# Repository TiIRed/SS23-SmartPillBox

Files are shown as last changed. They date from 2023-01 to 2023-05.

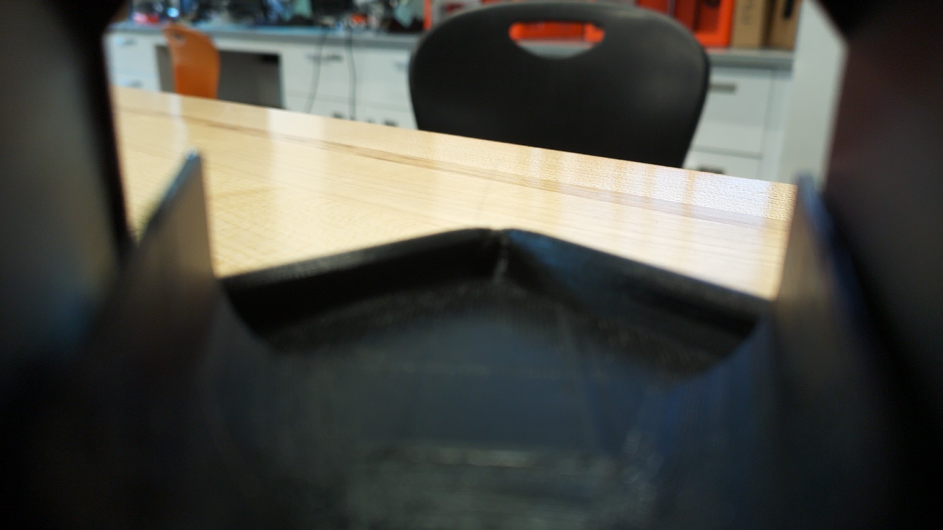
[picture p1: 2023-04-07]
Pi_Controls/test.jpg

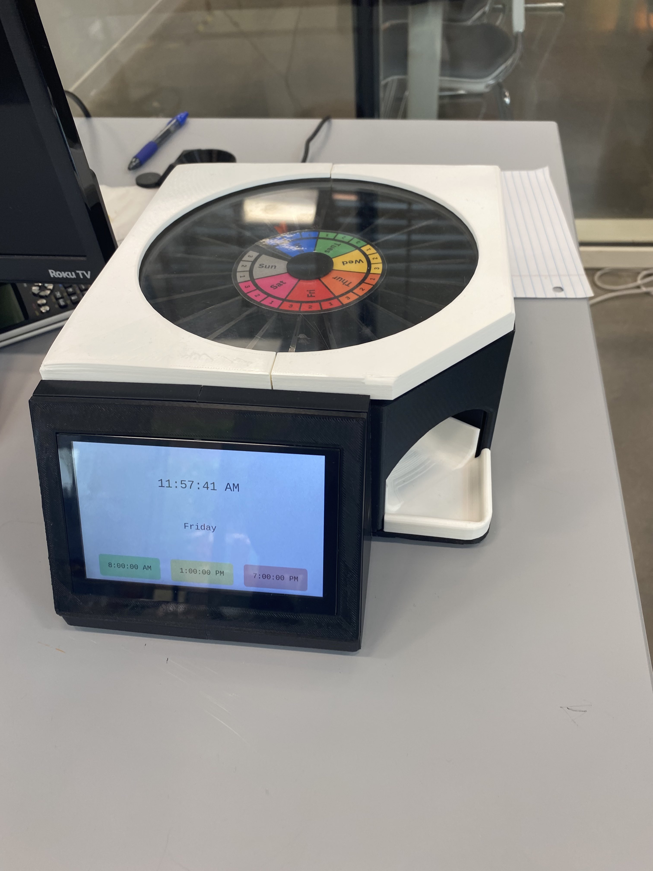
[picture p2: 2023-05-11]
Photos_Videos/IMG_7056.jpg

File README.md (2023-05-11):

# SS23-SmartPillBox

Pillbox
Download NodeJS at https://nodejs.org/en/download.
Navigate to the HTML folder and delete the node_modules folder and run "npm install" to install the modules again.
We found that when changing environments it was easier to install all of the modules again.

To start the program, run "npm run start".

The program can also be made into an executable by using electron forge (https://www.electronforge.io/) and can be compiled for a number of systems.

Server
First navigate to the ServerFile and run .venv\Scripts\activate to enter the virtual environment
For demonstration purposes and because we were unable to configure our server in the way that we like. The web app was deployed using waitress and can be called with the function "waitress-serve --call 'app:create_app'"

the storage variables are in appdata/roaming/html/config or home/.config/HTML
and when running npm on the pi you just have to do: rm node_modules && npm install

Database
Download PSQL from https://www.postgresql.org/download/ and make sure to Download PGAgent and PGBouncer from the stack builder
Next download pgAdmin at https://www.pgadmin.org/download/ this will let us manage the database.

Here you can create a new databse on the postgresql server that was just created. First I suggest creating a new user role that can access and edit the database.

For the included code I used the following SQL script
```
CREATE ROLE sfransen WITH
    LOGIN
    SUPERUSER
    INHERIT
    CREATEDB
    CREATEROLE
    NOREPLICATION
    PASSWORD Ladybug
```
Then I created the Database with:
```
CREATE DATABASE pillbox
    WITH
    OWNER = sfransen
    ENCODING = 'UTF8'
    LC_COLLATE = 'English_United States.1252'
    LC_CTYPE = 'English_United States.1252'
    TABLESPACE = pg_default
    CONNECTION LIMIT = -1
    IS_TEMPLATE = False;
GRANT TEMPORARY, CONNECT ON DATABASE pillbox TO PUBLIC;
GRANT ALL ON DATABASE pillbox TO sfransen;
```
Finally I created the tables with:
```
CREATE TABLE IF NOT EXISTS public.logins
(
    id bigint NOT NULL DEFAULT 'nextval('logins_id_seq'::regclass)',
    fname character varying(200) COLLATE pg_catalog."default" NOT NULL,
    lname character varying(200) COLLATE pg_catalog."default" NOT NULL,
    email character varying(200) COLLATE pg_catalog."default" NOT NULL,
    password character varying(200) COLLATE pg_catalog."default" NOT NULL,
    mtime time without time zone NOT NULL,
    mdtime time without time zone NOT NULL,
    etime time without time zone NOT NULL,
    CONSTRAINT logins_pkey PRIMARY KEY (id),
    CONSTRAINT logins_email_key UNIQUE (email)
)

TABLESPACE pg_default;
ALTER TABLE IF EXISTS public.logins
    OWNER to sfransen;
```
```
CREATE TABLE IF NOT EXISTS public.medications
(
    id bigint NOT NULL DEFAULT 'nextval('medications_id_seq'::regclass)',
    name character varying(200) COLLATE pg_catalog."default" NOT NULL,
    quantity bigint NOT NULL DEFAULT 'nextval('medications_quantity_seq'::regclass)',
    time_name character varying(200) COLLATE pg_catalog."default" NOT NULL,
    days text[] COLLATE pg_catalog."default" NOT NULL,
    username character varying(200) COLLATE pg_catalog."default",
    CONSTRAINT medications_pkey PRIMARY KEY (id)
)

TABLESPACE pg_default;
ALTER TABLE IF EXISTS public.medications
    OWNER to sfransen;
```
```
CREATE TABLE IF NOT EXISTS public.photos
(
    id bigint NOT NULL DEFAULT 'nextval('photos_id_seq'::regclass)',
    data bytea NOT NULL,
    "time" character varying(200) COLLATE pg_catalog."default" NOT NULL,
    username character varying(200) COLLATE pg_catalog."default" NOT NULL,
    dayofweek character varying(200) COLLATE pg_catalog."default" NOT NULL,
    CONSTRAINT photos_pkey PRIMARY KEY (id)
)

TABLESPACE pg_default;

ALTER TABLE IF EXISTS public.photos
    OWNER to sfransen;
```

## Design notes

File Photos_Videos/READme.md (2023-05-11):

Photos and Videos from the demonstration and assembly.

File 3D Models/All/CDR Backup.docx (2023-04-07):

Critical Design Review

ECEN 4024: Smart Pill Box Team

Spring 2023

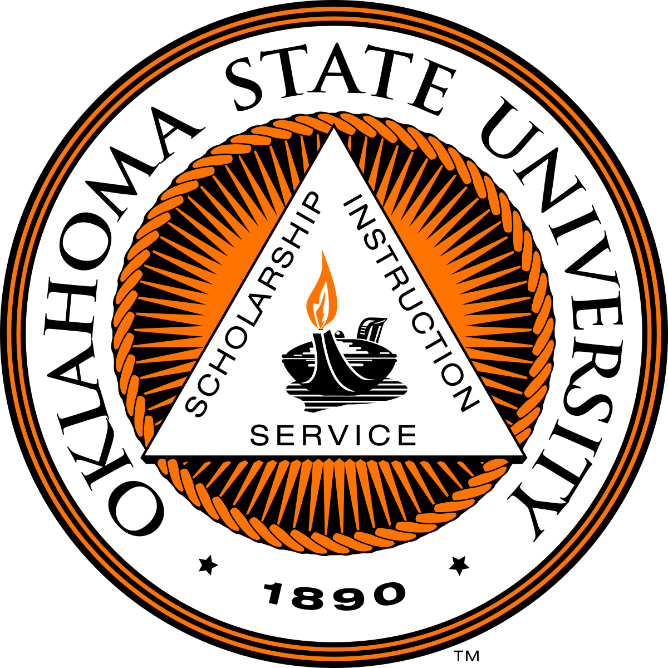
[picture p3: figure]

Report Presented by:

Zarek Rooker

Daniel Jacobs

Zahra Alnahwi

Stephen Fransen

Advisors:

Dr. Weihua Sheng, Joel Quarnstrom (GA), Su Zhidong (GA)

Electrical and Computer Engineering

Oklahoma State University

# 1. Team

## 1.1 Team Structure

- Zarek Rooker
  - Role: Hardware Manager & POC
  - Assignment: Hardware Design, Electronic Testing
- Zahra Alnahwi
  - Role: Circuit Designer:
  - Assignment: Electronic Design & Testing
- Stephen Fransen
  - Role: Backend Dev
  - Assignment: Software, Server Building
- Daniel Jacobs
  - Role: UI Designer:
  - Assignment: Software, User Interface

## 1.2 Advisors

The project is advised by Dr. Weihua Sheng and Graduate Assistants Joel Quarnstrom and Su Zhidong. Both graduate assistants offer advice and explanation. Joel offers advice in hardware design and testing while Su assists in electronic and software advice.

# 2. Problem Objective

The main vision of this project is to provide an efficient and safe way to manage medication for elderly patients, especially those with cognitive decline, memory loss, and visual impairments. The Smart Pill Box (SPB) can help them to take medication correctly and on time, reduce medication errors, and provide a better way for caregivers to monitor the medication adherence. The SPB can also provide a more convenient, user-friendly, and cost-effective solution compared to other existing solutions.

# 3. Design Constraints

## 3.1 Performance Constraints

The following specifications are the main driving point for our design throughout this document. Optional specifications are also listed below.

Specifications

1. Store medicine for 7 days and for morning, noon, and evening
2. Lock/Unlock mechanism for medication.
3. User interface with a touch screen
4. Speaker to remind the user to take medication.
5. Camera to capture images of the user taking medication.
6. Send notifications to caregivers upon completion of medication-taking.
7. Store medication data in a remote cloud server

Optional:

1. Recognize pill types and quantity through images taken by the camera (optional)
2. Support user authorization through face recognition or fingerprint (optional)

## 3.2 Economic Restraints

The design of the smart pill box should be cost-effective and accessible for customers. A hard budget of $1000 has been allocated to research and development for our project. To keep research and development within budget, our team aims to reduce the cost to around $500 to allow for potential contingency costs.

# 4. Ethical Responsibilities

## 4.1 Global

Global responsibilities for a smart pill box include meeting regulatory standards, safety requirements, and performance requirements. The pill box must ensure that it is compliant with all applicable laws and regulations and must be certified as meeting the applicable safety and performance requirements.

## 4.2 Economic

The economic responsibilities associated with a smart pill box are significant. It is important that the device is affordable for those who need it. This means that the device must have a low development cost to allow for appropriate production cost. Additionally, the device must be made with high-quality materials that will last for a long time.

## 4.3 Societal

The ethical responsibility for using these statistics is to ensure that elderly patients have access to their medications, are aware of how to use and manage them, and can take them safely. Additionally, the design should be intuitive and tailored to the elderly user to reduce the risk of medicine contamination and accidental ingestion. Lastly, it is important to provide education on how to use and manage medications, as well as the potential side effects, so that elderly patients can make the best decisions for their health.

## 4.4 Environmental

The user should also be aware of the materials used to make their Smart Pill Box. Our Smart Pill Boxes will be made with PLA, which is a biodegradable material. To protect the environment, the other materials used should be either biodegradable or recyclable. In addition, the Smart Pill Box should reduce the amount of energy used. The device should strive to utilize the lowest amount of energy possible. This will help to reduce energy waste and protect the environment.

# 5. Design Details

## 5.1 Electrical

## 5.2 Hardware

### 5.2.1 Introduction

The hardware components have multiple different sections that make up its design. We must consider the compartments that hold the pills, the locking mechanism, the overall housing design, and how to properly secure the device. This section will be broken down into five main sections: the Rotating Capsule Piece, Lid, Dispenser, Touchscreen Housing, and overall Housing. Each component is designed to be intuitive and user-friendly, utilizing materials that are both aesthetically pleasing and durable to ensure that the device is secure and stable. Furthermore, the design of the Smart Pill Box ensures that the medication is easily accessible and can be quickly refilled when necessary.

### 5.2.2 Overall Design

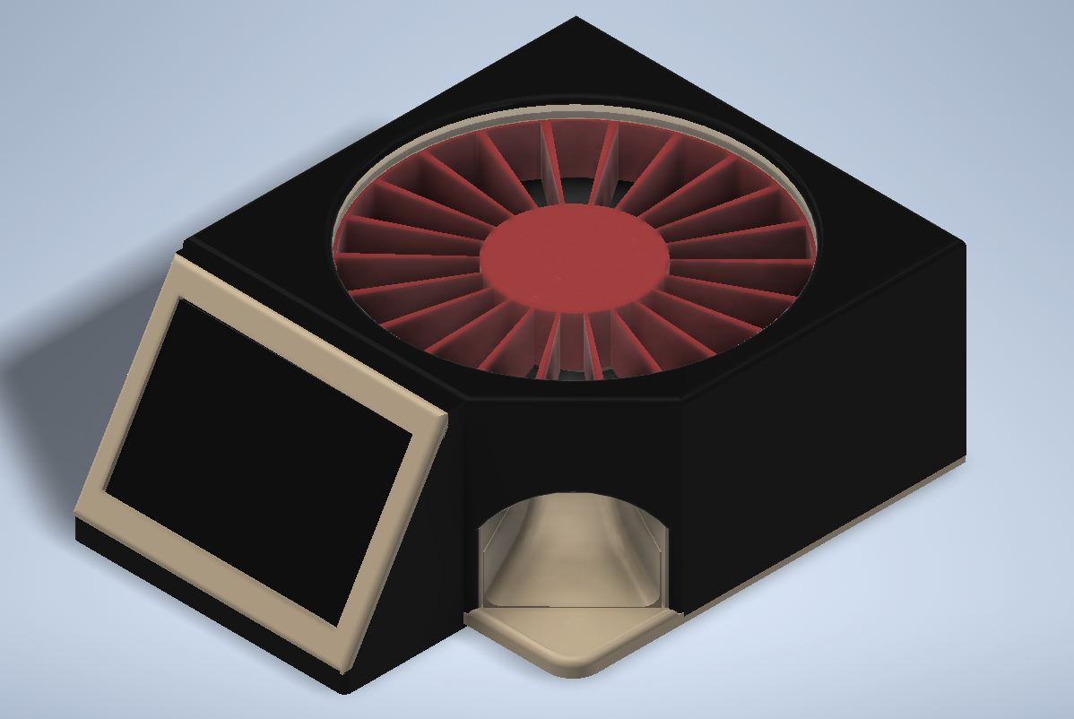
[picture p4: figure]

Figure 5.2.1: Overall Design

The overall design of the device can be seen in Figure 5.2.1. We will break down all the major components that make up the overall design, with a focus on visibility, easy loading, accessibility, and a 7-day supply. The dimensions of the design are 10” x 4” x 8” and the estimated weight is 3.283 lb. With this size, we can store more than 5 pills in one compartment, and loading is made easy with a lid that opens for mass loading. A touchscreen is featured on the front for user friendliness and the dispenser is clearly shown with an intuitive tray for the user to get pills from.

### 5.2.3 Rotating Capsule

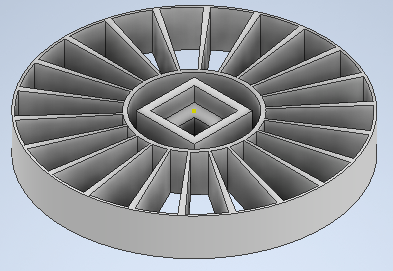
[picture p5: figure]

Figure 5.2.3: Rotating Capsule Piece (Bottom View)

The requirement for a locking mechanism pushed us to a design like the rotating capsule (Figure 5.2.2). The rotating capsule piece has 22 compartments for a 7-day supply to be held. The piece will sit on a stepper motor that will provide enough torque to rotate the device. The each cut out on the piece holds one time for taking medication (ex. Monday at 8 am). The device will also include a physical display of the day that it is on.

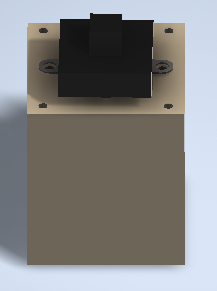
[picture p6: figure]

Figure 5.2.4: Motor Holder and Key

To allow for adjustments we are including a motor holder and motor key. Both pieces allow us to verify the fit of the motor and the fit of the axle. This allows for easy adjustment and reduces 3D print times. As we can see in Figure 6.2.4 the motor holder is the gray piece and will include cutouts for the wires of the stepper motor to come out. It also has 4 screw holes to allow the drop plate to connect. The motor key is the black piece and fits into the rotating capsule piece (Figure 6.2.3). These pieces have already been printed but are already subject to change. Specifically, they will be adjusted to host ball bearings.

### 5.2.4 Lid & Locking Mechanism

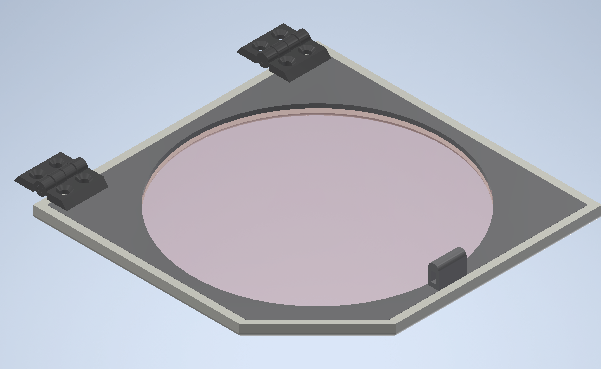
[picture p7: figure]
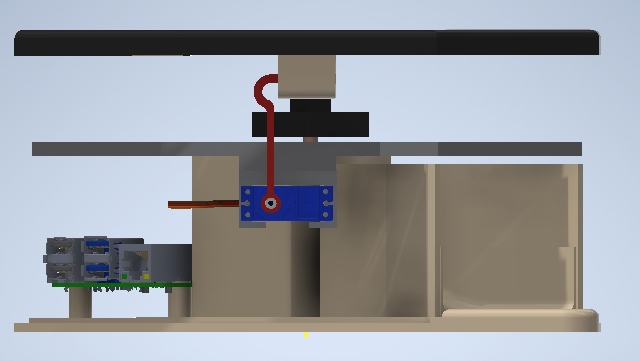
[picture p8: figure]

Figure 5.2.4: Lid and Locking Mechanism

This lid mechanism is designed with a three-part system (Figure 5.2.4, Left). The first part is the top piece which is the outside of the box. The second part is a clear portion, which provides a clear view of the contents inside smart pill box. The third part is at the bottom plate of the lid and will allow for a flush finish that keeps all the components of the lid secured. The top lid is made of durable material and the lid support ensures that the lid remains in place. The locking mechanism is a simple hook design, which allows the user to easily lock and unlock the mechanism (Figure 5.2.4, Right). This will be controlled by the touchscreen, which allows for easy access to the locking mechanism. This locking mechanism is the perfect solution for securing the pills and keeping them safe.

### 5.2.5 Dispenser & Tray

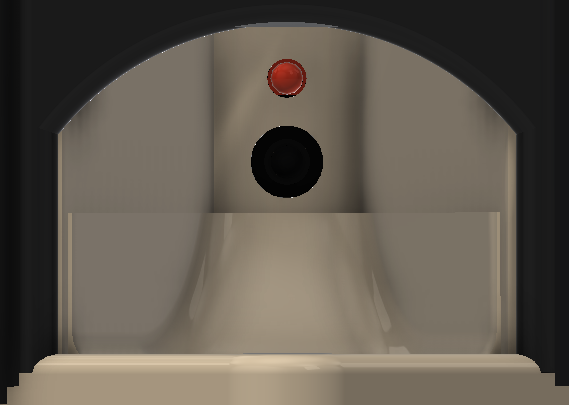
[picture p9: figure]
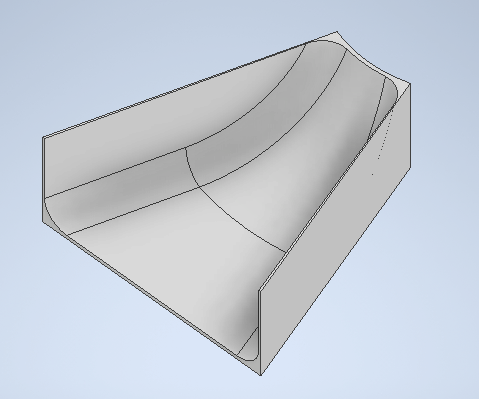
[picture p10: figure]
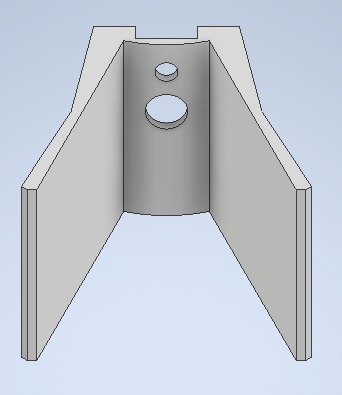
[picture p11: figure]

Figure 5.2.5: Dispenser & Tray

The dispenser of the Smart Pill Box will have multiple features (Figure 5.2.5, Left). It will be made of a baseplate and camera holder, and the opening will be 3 inches wide, big enough for most hand sizes to fit into. There will also be a tray that allows for the medicine to be removed and cleaned more easily (Figure 5.2.5, Middle). Inside the dispenser, a camera will be housed to take before and after pictures of the medicine being taken from the compartment. The camera will be held and secured in the camera holder (Figure 5.2.5, Right), and an LED will provide better visibility and clarity of where the medicine is dispensed.

### 5.2.6 Touchscreen Housing

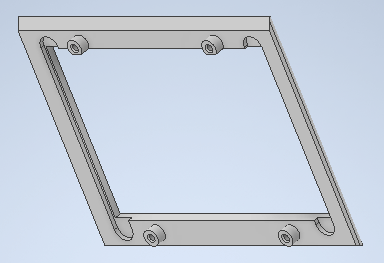
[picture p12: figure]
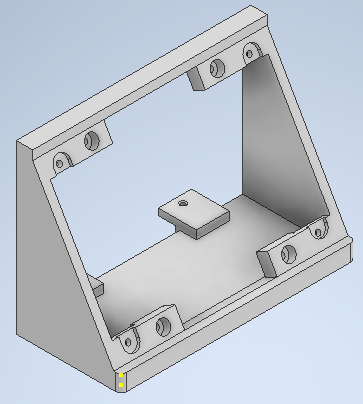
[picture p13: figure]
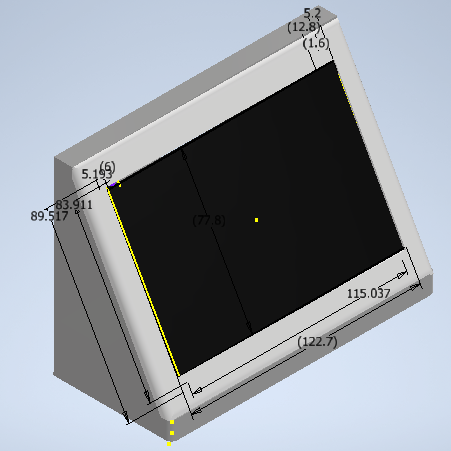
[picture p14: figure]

Figure 5.2.6: Touchscreen Housing Parts

The touchscreen housing (Right) also has three components: a faceplate (Left), a touchscreen holder (Middle), and a 5” touchscreen. The design was created to introduce a finishing touch to the holder. The faceplate will be placed on the front of the holder to present a flush finish with no screw holes visible. The 5” touchscreen will be securely inserted into the holder and will support all the necessary connectivity. The connections will all be hidden at the back and out of view from the user. The touchscreen will be set at a 60-degree angle to enable the user to clearly see the device even if it is at waist height. The overall holder design will connect to the overall housing to provide a finished look.

### 5.2.7 Overall Housing

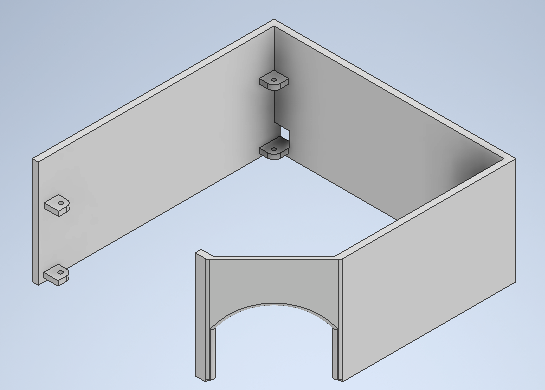
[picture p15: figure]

Figure 5.2.7: Housing Walls

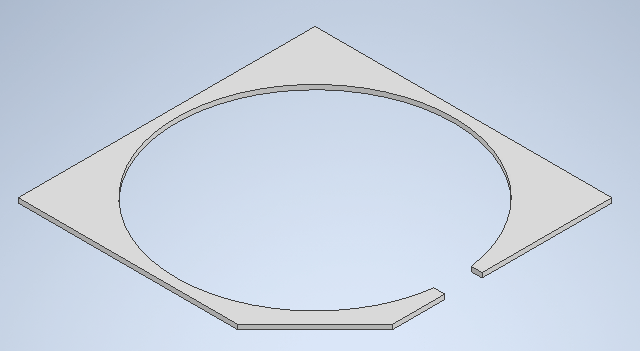
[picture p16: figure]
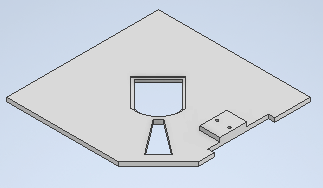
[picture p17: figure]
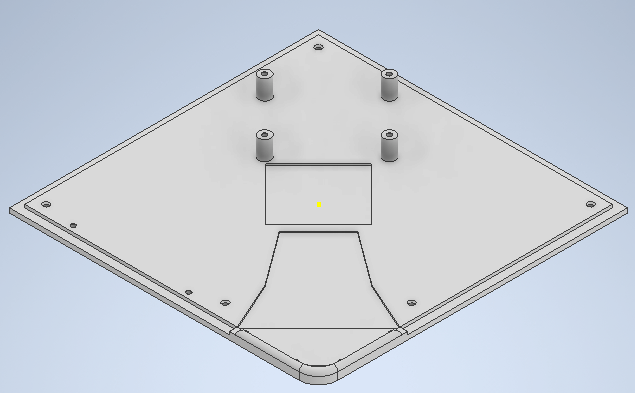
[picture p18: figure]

Figure 5.2.8: Top Plate, Drop Plate, and Bottom Plate

The overall housing consists of the walls (Figure 5.2.7) and baseplates (Figure 5.2.8). The wall of the design is very simple and will have a cutout to allow for power to connect to the system. The baseplates will have three components the top plate, drop plate, and baseplate. The top plate will be flush with the rotating capsule and will be visible when the lid is open. The drop plate is where the pills will be dispensed and will hold all the pills on it. It will also hold the place the servo will be used to lock the device. Finally, the baseplate is the bottom of the project and will have rubber feet to secure the device onto any surface. The two components will be connected by screws, bolts, and nuts to allow for an accurate finish.

## 5.3 Software

# 6. Testing Strategy and Results

## 6.1 Electrical

## 6.2 Hardware

Testing the hardware for a smart pill box is an important part of the manufacturing process. The hardware must meet certain standards to ensure the device is safe and reliable. This usually involves testing the connections of the components, checking for any potential malfunctions, and testing the overall design of the device. Additionally, the hardware must be tested for its durability and ability to withstand any potential external forces. Through these tests, we can ensure that the smart pill box is safe and reliable for its intended purpose.

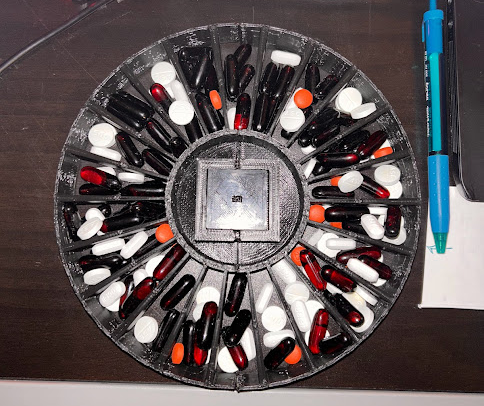
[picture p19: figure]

Figure 6.2.1: 3D Printed Rotary Capsule

With 3D Printed parts connections always seem to be a problem. We have already tested the screw fittings, bolt fittings, and the size of the overall model. Figure 6.2.1 shows the size of the rotating capsule. The image depicts the number of pills that can fit in each slot, and it is easily over 5 pills.

Initial hardware testing we have already conducted include testing the motor torque to see if it can support the rotating capsule piece. The test was successful, and we have already learned how to increase performance. The biggest solution is to reduce the friction coefficient. This can be done by having a lighter model, ball bearings or ball rollers, and potentially a different material with a lower friction coefficient.

## 6.3 Software

# 7. Cost

## 7.1 Cost Breakdown

## 7.2 Parts List

# 8. Scheduling

## 8.1 Initial Schedule

## 8.2 Current Schedule

# 9. Risk Management

# 10. Report Contributions

# 11. References

ECEN 4024 Project SPB Spring 2023

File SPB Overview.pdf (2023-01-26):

Parts: | Cost: | Description: | Link:
Raspberry Pi 4B | | Microcontroller
7-inch touch screen | | 7-inch touch screen
| | Speaker
| | Mini Camera

Specifications:
Multiple Compartments
- Led showing when it is time to take them.
- Speaker ringtone to remind user to take medicine

•

- Lockable
Store medicine for 7 days of the week
- Morning, noon, and evening

•

User interface
Touch screen
- Use it to unlock and access pills

○

Take photos before and after
- Saved in database (remote cloud server)

○

- Notification sent to caregiver after completion

•

Optional:
- Face recognition or finger print
- Cloud server to store medication data and connect to caregiver
- Mobile app to allow medication schedules and view medication info
- Recognition of pill types and quantity images taken by the camera

Major Components:
Hardware
- Compartments
- Box Design
- Housing for Raspberry Pi

•

Software
- Remote Cloud Server
- User Interface (UI)
- Notifying Caregiver
- Photo Capture

•

Electrical
- Components (Pi, Camera, Speaker…)
- Locking/Unlocking Mechanism
- LED Lighting

•

# Smart Pill Box (SPB)

Tuesday, January 17, 2023 6:11 PM

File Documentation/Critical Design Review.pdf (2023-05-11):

# Critical Design Review

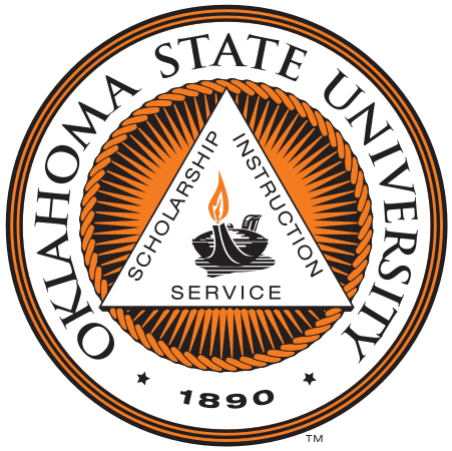
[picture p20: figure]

# Smart Pill Box

Oklahoma State University
Senior Design Spring 2023

# Overview

Introduction
Project Description
Constraints
Electrical Components • Parts

Hardware Design • Components • Testing

Software Design • Frontend & Backend

Cost Analysis
Project Plan
Risk Management
Hazard Analysis
Work Distribution
Questions

Zarek Rooker

# Team Introductions and Roles

Assignment:
- Component Research
- Hardware
- Electronics

Backend Dev:
- Stephen Fransen
E.E

Zarek Rooker

UI Designer:
- Daniel Jacobs
C.E.

Assignment:
- Software
- Server Building

Assignment:
- Software
- User Interface

Circuit Designer:
- Zahra Alnahwi
E.E

Hardware Manager:
- Zarek Rooker
E.E & C.E.

Assignment:
- Point of Contact
- Hardware
- Electronics

# Project Description

## Project Vision:

The main vision of this project is to provide an efficient and safe way to manage medication for elderly patients, especially those with cognitive decline, memory loss, and visual impairments. The Smart Pill Box (SPB) can help them to take medication correctly and on time, reduce medication errors, and provide a better way for caregivers to monitor the medication adherence. The SPB can also provide a more convenient, user-friendly, and cost-effective solution compared to other existing solutions.

Zarek Rooker

# Design Constraints

Specifications
1. Store medicine for 7 days and for morning, noon, and evening
2. Lock/Unlock mechanism for medication
3. User interface with a touch screen
4. Speaker to remind the user to take medication
5. Camera to capture images of the user taking medication
6. Send notifications to caregivers upon completion of medication-taking
7. Store medication data in a remote cloud server
Optional:
1. Recognize pill types and quantity through images taken by the camera (optional)
2. Support user authorization through face recognition or fingerprint (optional)

Zarek Rooker

# Consideration and Constraints

Statistics to Consider:
- Average Adult takes 4 prescription medication
- More than four in ten older adults take five or more prescription medications

Target Audience:
- Elderly Patients

Considerations:
- Ease of use: The design should be intuitive and easy to operate, allowing elderly users to quickly and easily access their medication
- Lower risk of medicine contamination
- Lower risk of accidental ingestion of medication
- Accommodating for all

Zarek Rooker

# Consideration and Constraints

Environmental:
- Energy efficient.
- Recyclable/Compostable

Health:
- Safe for Use
- Properly Locking
- List Medications

Safety:
- Electrical shock or fire
- Sharp edges & hazards

Sustainability:
- Long life span
- Refurbish/Reusable

Social:
- Accessible and useable for all

Cultural:
- Appropriate for target
audience

Global:
- Meets regulatory standards
- Meets safety and
performance requirements

Ethical:
- Ethically produced and
sourced

Professional:
- Meets industry standard

Zarek Rooker

# Schematic

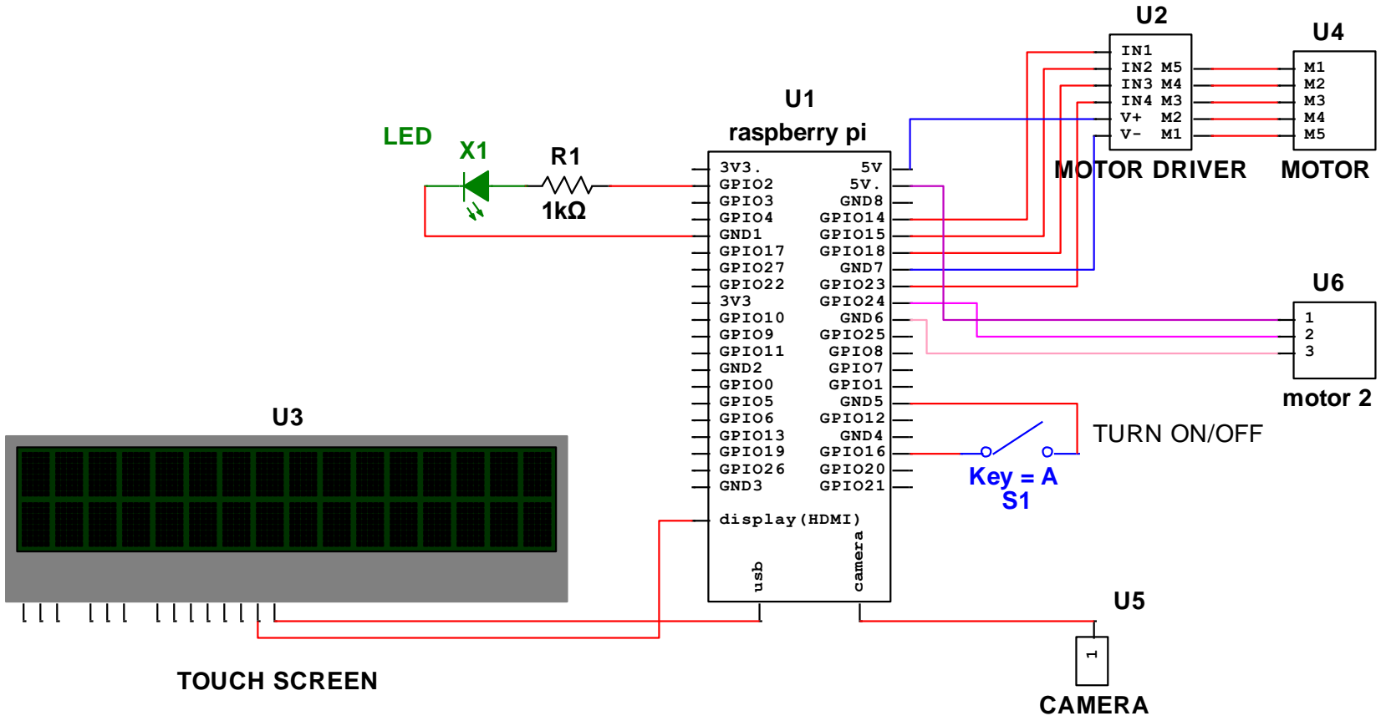
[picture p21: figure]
U1 raspberry pi; 3V3. GPIO2 GPIO3 GPIO4 GND1 GPIO17 GPIO27 GPIO22 3V3 GPIO10 GPIO9 GPIO11 GND2 GPIO0 GPIO5 GPIO6 GPIO13 GPIO19 GPIO26; GND3; GPIO21; GPIO20; GPIO16; GND4; GPIO12; GND5; GPIO1; GPIO7; GPIO8; GPIO25; GND6; GPIO24; GPIO23; GND7; GPIO18; GPIO15; GPIO14; GND8; camera; usb; display(HDMI); CAMERA; MOTOR DRIVER; MOTOR; X1 LED; Key = A; TURN ON/OFF; motor 2; TOUCH SCREEN

Zahra Alnahwi

# Pins Layout

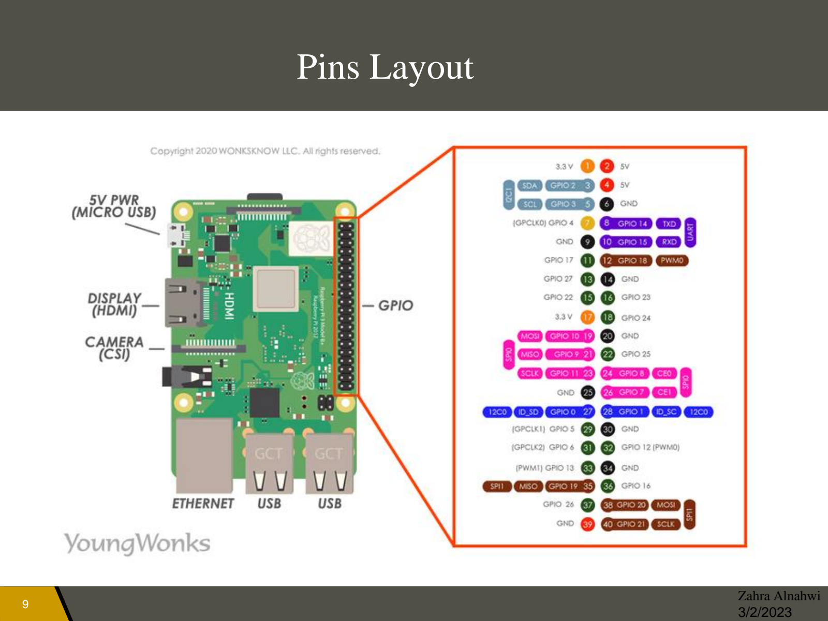
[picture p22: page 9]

Zahra Alnahwi

## POWER CONSUMPTION

Zahra Alnahwi

## Raspberry pi Power Requirement

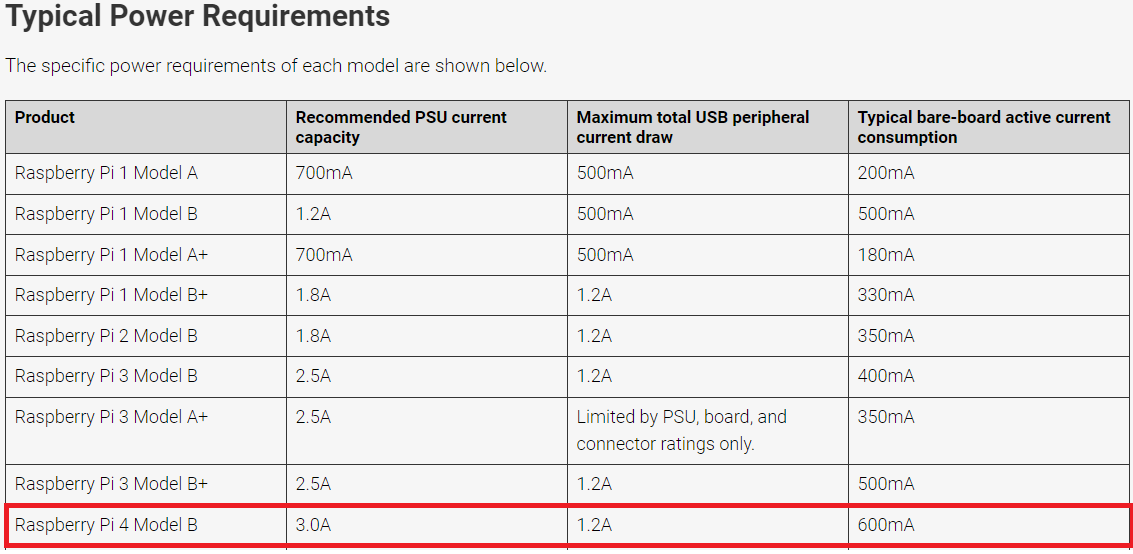
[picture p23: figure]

Zahra Alnahwi

## Raspberry pi Power Requirement

Boot State: is the state when the Raspberry Pi is starting up
Idle State: is the state where the Raspberry Pi is on but not doing anything
Stress State: Stress testing is simply running a series of processes on your
system which are designed to run the CPU at full power, and monitor the
temperature and stability of the system. | Zahra Alnahwi

# Microcontroller

RASPBERRY PI 4B/4GB

- Can run on 5V/3A DC or 5.1V/ 3A DC
- 40 Digital I/O Pins

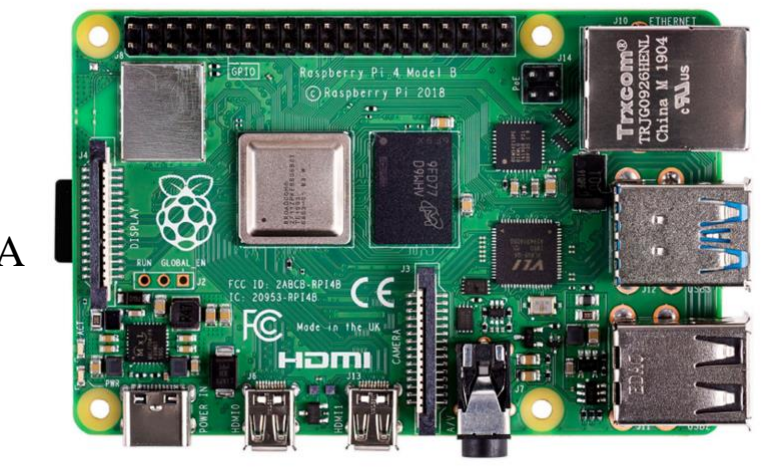
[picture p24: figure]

- Each GPIO pin could output up to 16mA at 3.3 V
- All GPIO pins together should not
exceed 50mA
- Programmed using python | $149

Zahra Alnahwi

# Touch Screen and Speaker

5” Touch screen

- Touchscreen IPS Display 800x480 USB Powered HDMI Monitor
- Built-in Speaker & Stand for Raspberry Pi Jetson Nano Win PC
- Unite weight : 8.1 ounces

Zahra Alnahwi

$61.99

# Camera

Raspberry Pi Camera Module 3

- Power consumption : 0.4 W – 1.4W
- The camera uses power supply from the Raspberry Pi
- Resolution: 11.9 megapixels

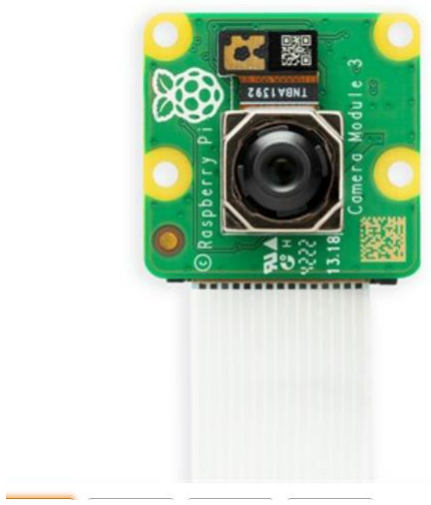
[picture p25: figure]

$25

Zahra Alnahwi

# Motor 1

$14.99

Stepper Motor

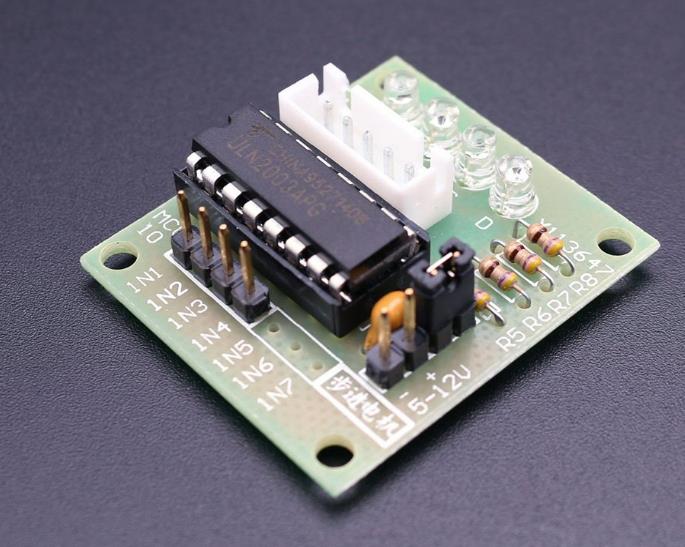
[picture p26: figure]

Zahra Alnahwi

- The motor will connect to the driver motor
- The motor and the driver need 5V input
- Both draw 240mA
- Unite weight : 10.4 Ounces

## Motor 2

DFRobot Accessories TowerPro SG90C 360 Degree Micro Servo


$4

- the motor need 5V input
- The motor draw 10mA
- Unite weight : 0.352740 oz

Zahra Alnahwi
3/2/23

## LED

- 1K Ohm resistor
- LED (60mA)


Zahra Alnahwi

## Power Switch

Push Button Switch

- The Raspberry Pi does not have a power button
- Users cannot just unplug the Raspberry from the wall. By doing that, anything that’s written to the memory will become corrupted.
- Connect the switch (Normally Open SPST) to 1 GPIO pin and 1 GND pin
- Write a script on the Raspberry Pi to safely shut it down when the button is pressed
- Once the switch is pressed, it will run a script that’s on the Raspberry Pi that will safely shut it down


Zahra Alnahwi

# Power Supply

Official Raspberry Pi Power Supply 5.1V 3A with USB C - 1.5 meter long

$7.98

Zahra Alnahwi

# Final Design Expectation

Features:
- Rotating Disk Capsules
- Clear Locking Lid
- Mass Loading
- Physical Labels
- 7 Day Supply
Size: 10” x 4” x 8”

Weight: 3.283 lb
Main Components:
- Capsule Piece
- Lid
- Dispenser
- Touchscreen Housing
- Overall Housing


Zarek Rooker

# Electronics/Mechanics

Features:
- Camera in Dispenser
- Secured Raspberry Pi
- Stepper Motor & Servo Motor
- LED in Dispenser
- Touch Screen


Parts Not Shown:
- Wires
- Pi Fan
- Power button/Reset Switch
- Power Cord
- Screws (#4-40)

Zarek Rooker

# Rotating Capsule

Features:
- Rotating Capsule

– 22 Compartments
- Motor Holder

– Holds 5V Servo
- Motor Key

– Adjustable Part

Zarek Rooker

# Lid & Locking Mechanism


Features:
- Locking Mechanism
– Simple Hook Design
– Touchscreen Control
- Three Separate Parts
– Clear Portion
– Top Lid
– Lid Support

Zarek Rooker

# Dispenser/Tray

Features:
- Dispenser

– Baseplate, Camera Holder (Drop Spot) – 3 Inch Opening
- Camera

– Tilted to See Pills
– (Testing Needed For Position)
- Slide/Tray

– 1.5 Inch Extension Out
- LED

Zarek Rooker

# Touchscreen Housing


Features:
- Three Part Set

– Faceplate
– Touchscreen Holder
– 5” Touchscreen
- 60 Degree Angle

Zarek Rooker

# Overall Housing

Features:
- Walls
- Baseplates (3)

– Top Plate
– Drop Plate
– Base Plate
- Rubber Feet
- Connection Points

Zarek Rooker

# Hardware Overview

Components:
- Total Parts ~16
Hardware Testing Done:
- Tested Motor Torque
- Motor Key Fitting, Screw Fitting, Bolt Fitting
- Parts Tested:
– | Rotating Capsule
– | Motor Holder
In Progress:
- Fabrication
- Alignment For Models
- Fixing Small Model Errors
- Finish Parts (2)


To Do:
- Camera Position, Tray Piece Testing

Zarek Rooker

# Torque Testing

Torque:
- Holding Torque: 150 gram-force*cm, 15 N*mm/ 2 oz-force*in

– (Measure that keeps the motor from moving)


Solutions To Increase Performance:
- Reduce Friction Coefficient

– Lighter Model
– Ball Bearings & Ball Rollers – Different Material

Zarek Rooker

# Software Design

Stephen Fransen; Webapp Server; SPB; Caregiver; Database; Remote Server; Motor Control

# Software Design - SPB

Stephen Fransen

## Motor Control

We will be using Electron to create the UI for the Smart Pillbox
- Uses HTML 5 and JavaScript
- Ease of Use
- Open-Source
- Access to DB


Advantages:
- Experience using HTML, CSS, and JavaScript
- Use same languages for local UI and website
Disadvantages:
- May be some design quirks

# Software Design – Remote Server

Stephen Fransen

Webapp Server; Database

We have decided to move to a Remote Server
- Secure
- Unified Log-in
We are using Flask as the framework for our webapp and serving it through a combination of Gunicorn and NGINX
- Flask is a native WSGI application framework
- Gunicorn will serve the webapp
- NGINX will act as a reverse proxy and receive HTTP calls more securely and effectively

PostgreSQL will serve as our DB
- Secure
- Multi-Access

# User Interface Design

Desired Outcome:
- Simplicity
- Easy to Use
Required Features:
- Touch screen

– Use it to unlock and access pills
- Take photos before and after

– Saved in database (remote cloud server)
- Notification sent to caregiver after completion

Concerns:
- Missed Medication
– Beep for 20 Minutes
– Notify Caregiver

Daniel Jacobs

# User Interface Design

Always on Display:
- Date
- Time
- Schedule Time

Zarek & Daniel

## MONDAY

8:15:10 AM | 2/2/2023

Evening:
10:00 pm

Night:
8:00 pm

Morning:
8:15 am

Alert Display:
- Unlocks on Interaction
- Settings
- Snooze Alarm
- Time
- Schedule Time

# User Interface Design

Distribution Display:; • Medication List; • Live Camera View; • Unlocks on Interaction; Pills Distributed; Take; Medication List: • A • B • C; Camera; Notifying Caregiver; Before:; Next Time: 12:00PM After:; DONE; Acknowledgement Display:; • Confirmation Message; • Next Medication Time; • Before & After Picture

Zarek & Daniel

# Web Application Features

Web/Phone Application
- Medication Notifications

– Notified if patient has/has not taken their medication yet
– List patient’s medication for upcoming period

Stephen Fransen

Morning:
8:15 am

Evening:
10:00 pm

Night:
8:00 pm

Patient has not taken their morning medication

Patient’s Morning
Medication
- A
- B
- C
- D

# Web Application Features

Web/Phone Application
- Medication Notifications

– Notified if patient has/has not taken their medication yet
– List patient’s medication for upcoming period
- Medication Confirmation

– Confirm patient has taken medication – Confirm correct medication has been dispensed

Morning: 8:15 am; Evening: 10:00 pm; Night: 8:00 pm; Patient’s Morning Medication • A • B; Medication Confirmation; Before; After

Stephen Fransen

## Software Testing Methods

## Planned testing:

- Proper hardware control
- Interface responsiveness
- Server connection

– Raspberry Pi sending information

– Caregiver receiving information
- Website functionality
- Login security

## Design Cost Analysis

Zarek Rooker

Parts: | Cost: | Parts: | Cost:
Raspberry Pi 4B | $200 | Screws/Bolts/Nuts | $7.8
Pi Cord | $8 | Cable USB | $6.12
Touchscreen | $100 | Cable HDMI | $3.00
Camera | $25 | Hinge(2) | $4.53
Stepper Motors | $22 | SD Card | $10.81
Servo Motor | $4
Ball Bearings (4) | $1 | Total Cost: | $399.26

Future Contingency Costs: >$50

Touchscreen and Pi make up 75% of cost
Production cost given purchases in bulk and utilizing any vendor. ~$250

# Project Plan


Stephen Fransen

# Project Plan


Stephen Fransen

# Risk Management

| Negligible | Minor | Moderate | Significant | Severe
Very Likely | | | 3D Printer Failure
Likely | | | | Server/Networking Issues
Possible | Motor Failure | Selected Parts are Unavailable | Broken Parts/Screens
Unlikely | | | | Design Does Not Meet Specification

Very Unlikely

Impact

Likelihood

Stephen Fransen

# Hazard Analysis

Wrong Drug Dosage: Smart pill boxes may have inaccurate dosages if users forget to double-check their input or if the machine malfunctions

Mitigation Strategy:
Keep and display a record of all medications taken and dosages.

Malfunctioning: The smart pill box may malfunction due to programming errors, hardware issues, or power outages, leading to incorrect prescriptions being dispensed.

Mitigation Strategy:
Regularly check and maintain the device to ensure it is functioning properly. Implement a redundancy system that can detect any errors and alert the user.

Zarek Rooker

# Hazard Analysis

Accidental Overdose: Overdose of medication due to incorrect dosage settings or incorrect usage of the device.

Mitigation Strategy: Educate users on how to use the device correctly, including instructions on how to set the dosage, and provide an emergency contact number in case of accidental overdose. The smart pill box should be programmed to alert the user if too many doses are taken in a day.

Security and privacy risks: Data stored on the device may be accessed by unauthorized users.

Mitigation Strategy: Utilize encryption technology to protect user data from being accessed by unauthorized users and to prevent data tampering. Additionally, provide a secure login system with password protection.

Zarek Rooker

# Presentation Work Disbursement

Zarek- Description, Design Constraints, Considerations, Hardware Design, Torque Calculations, Hazard Analysis

Zahra- Parts Research, Price Research , Power consummption, and Schematic

Stephen- Risk Management, Software Design, Project Plan, Web Application Features

Daniel – Testing, Decision Matrix, and Experimentation

# Questions?

# Reference Material


Weight from Inventor and
Center of Gravity
Name | Quantity | Price
Raspberry Pi | 1 | $55.00
Display | 1 | $100.00
Camera | 1 | $35.94
Speaker | 1 | $13.00
Motor | 7 | $14.00
Adafruit DC & Stepper Motor | 1 | $22.50
Power | 1 | $12.50
Total Price | $323.94
Proposed Cost | $400.00

Initial Cost Estimate

# References:

Prescription drug statistics 2022 (singlecare.com) (https://www.singlecare.com/blog/news/prescription-drug-statistics/)

Medication overload and older Americans -Lown Institute (https://lowninstitute.org/projects/medication-overload-how-the-drive-to-prescribe-is-harming-older-americans/)

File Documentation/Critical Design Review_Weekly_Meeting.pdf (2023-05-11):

# Critical Design Review


# Smart Pill Box

Oklahoma State University
Senior Design Spring 2023

# Overview

Introduction
Project Description
Constraints
Electrical Components
- Parts
Software Design
- Frontend & Backend
Hardware Design
- Design I, Design II, and Alternatives Design Analysis & Decision Matrix Testing and Experimentation Project Plan
Risk Management
Hazard Analysis
Cost
Work Distribution
Questions

Zarek Rooker

# Team Introductions and Roles


Assignment:
- Component Research
- Hardware
- Electronics

Backend Dev:
- Stephen Fransen
E.E

UI Designer:
- Daniel Jacobs
C.E.

Assignment:
- Software
- Server Building

Assignment:
- Software
- User Interface

Circuit Designer:
- Zahra Alnahwi
E.E

Hardware Manager:
- Zarek Rooker
E.E & C.E.

Assignment:
- Point of Contact
- Hardware
- Electronics

# Project Description

## Project Vision:

The main vision of this project is to provide an efficient and safe way to manage medication for elderly patients, especially those with cognitive decline, memory loss, and visual impairments. The Smart Pill Box (SPB) can help them to take medication correctly and on time, reduce medication errors, and provide a better way for caregivers to monitor the medication adherence. The SPB can also provide a more convenient, user-friendly, and cost-effective solution compared to other existing solutions.

# Design Constraints

Specifications
1. Store medicine for 7 days and for morning, noon, and evening
2. Lock/Unlock mechanism for medication
3. User interface with a touch screen
4. Speaker to remind the user to take medication
5. Camera to capture images of the user taking medication
6. Send notifications to caregivers upon completion of medication-taking
7. Store medication data in a remote cloud server
Optional:
1. Recognize pill types and quantity through images taken by the camera (optional)
2. Support user authorization through face recognition or fingerprint (optional)Multiple Compartments to store medicine

# Consideration and Constraints

Statistics to Consider:
- Average Adult takes 4 prescription medication
- More than four in ten older adults take five or more prescription medications

Target Audience:
- Elderly Patients

Considerations:
- Ease of use: The design should be intuitive and easy to operate, allowing elderly users to quickly and easily access their medication
- Lower risk of medicine contamination
- Lower risk of accidental ingestion of medication
- Accommodating for all

# Consideration and Constraints

Environmental:
- Energy efficient.
- Recyclable/Compostable

Health:
- Safe for Use
- Properly Locking
- List Medications

Safety:
- Electrical shock or fire
- Sharp edges & hazards

Sustainability:
- Long life span
- Refurbish/Reusable

Social:
- Accessible and useable for all

Cultural:
- Appropriate for target
audience

Global:
- Meets regulatory standards
- Meets safety and
performance requirements

Ethical:
- Ethically produced and
sourced

Professional:
- Meets industry standard

# Schematic

U1 raspberry pi; 3V3. GPIO2 GPIO3 GPIO4 GND1 GPIO17 GPIO27 GPIO22 3V3 GPIO10 GPIO9 GPIO11 GND2 GPIO0 GPIO5 GPIO6 GPIO13 GPIO19 GPIO26; GND3; GPIO21; GPIO20; GPIO16; GND4; GPIO12; GND5; GPIO1; GPIO7; GPIO8; GPIO25; GND6; GPIO24; GPIO23; GND7; GPIO18; GPIO15; GPIO14; GND8; camera; usb; display(HDMI); CAMERA; MOTOR DRIVER; MOTOR; X1 LED; Key = A; TURN ON/OFF; motor 2; TOUCH SCREEN

Zahra Alnahwi

# Pins Layout


Zahra Alnahwi

# Microcontroller

RASPBERRY PI 4B/4GB

- Can run on 5V/3A DC or 5.1V/ 3A DC
- 40 Digital I/O Pins
- Each GPIO pin could output up to 16mA at 3.3 V
- All GPIO pins together should not
exceed 50mA
- Programmed using python | $149

Zahra Alnahwi

# Touch Screen and Speaker


5” Touch screen

- Touchscreen IPS Display 800x480 USB Powered HDMI Monitor
- Built-in Speaker & Stand for Raspberry Pi Jetson Nano Win PC
- Unite weight : 8.1 ounces

Zahra Alnahwi

$61.99

# Camera

Raspberry Pi Camera Module 3

- Power consumption : 0.4 W – 1.4W
- The camera uses power supply from the Raspberry Pi
- Resolution: 11.9 megapixels


$25

Zahra Alnahwi

# Motor 1


$14.99

Stepper Motor


Zahra Alnahwi

- The motor will connect to the driver motor
- The motor and the driver need 5V input
- Both draw 240mA
- Unite weight : 10.4 Ounces

## Motor 2

DFRobot Accessories TowerPro SG90C 360 Degree Micro Servo

$4

- the motor need 5V input
- The motor draw 100 – 250mA
- Unite weight : 0.352740 oz

Zahra Alnahwi

## LDE


- 1K Ohm resistor
- LED


Zahra Alnahwi

## Button Turn on/off


Push Button Switch

- Current Rating : 1A
- Operating Voltage : 250V
- Contact : normally Open
- Brand : Push Button

Zahra Alnahwi

# Power

Official Raspberry Pi Power Supply 5.1V 3A with USB C - 1.5 meter long


$7.98

Zahra Alnahwi

# Software Design

Stephen Fransen; Server; SPB; Caregiver

# User Interface Design

Desired Outcome:
- Simplicity
- Easy to Use
Required Features:
- Touch screen

– Use it to unlock and access pills
- Take photos before and after

– Saved in database (remote cloud server)
- Notification sent to caregiver after completion

Concerns:
- Missed Medication
– Beep for 20 Minutes
– Notify Caregiver

Daniel Jacobs

# User Interface Design

Always on Display:
- Date
- Time
- Schedule Time

Zarek & Daniel

## MONDAY

8:15:10 AM | 2/2/2023

MORNING PILLS; Take

Evening:
10:00 pm

Night:
8:00 pm

Morning:
8:15 am

Alert Display:
- Unlocks on Interaction
- Settings
- Snooze Alarm
- Time
- Schedule Time

# User Interface Design

Distribution Display:; • Medication List; • Live Camera View; • Unlocks on Interaction; Pills Distributed; Take; Medication List: • A • B • C; Camera; Notifying Caregiver; Before:; Next Time: 12:00PM After:; DONEE; Acknowledgement Display:; • Confirmation Message; • Next Medication Time; • Before & After Picture

Zarek & Daniel

# Web Application Features

Web/Phone Application
- Medication Notifications

– Notified if patient has/has not taken their medication yet
– List patient’s medication for upcoming period

Stephen Fransen

Morning:
8:15 am

Evening:
10:00 pm

Night:
8:00 pm

Patient has not taken their morning medication

Patient’s Morning
Medication
- A
- B
- C
- D

# Web Application Features

Web/Phone Application
- Medication Notifications

– Notified if patient has/has not taken their medication yet
– List patient’s medication for upcoming period
- Medication Confirmation

– Confirm patient has taken medication – Check on patient’s current condition

Stephen Fransen

Morning:
8:15 am

Evening:
10:00 pm

Night:
8:00 pm

Patient’s Morning
Medication
- A
- B

Medication Confirmation
Before | After

# Final Design Expectation


Features:
- Rotating Disk Capsules
- Clear Locking Lid
- Mass Loading
- Physical Labels
- 7 Day Supply
Size:
- 10” x 4” x 8”
Main Components:
- Capsule Piece
- Lid
- Dispenser
- Touchscreen Housing
- Overall Housing

# Electronics/Mechanics

Features:
- Camera in Dispenser
- Secured Raspberry Pi
- Stepper Motor & Servo Motor
- LED in Dispenser
- Touch Screen


Parts Not Shown:
- Wires
- Pi Fan
- Power button/Reset Switch
- Power Cord
- Screws (#4-40)

# Rotating Capsule


Features:
- Rotating Capsule

– 22 Compartments
- Motor Holder

– Holds 5V Servo
- Motor Key

– Adjustable Part

# Lid & Locking Mechanism


Features:
- Locking Mechanism
– Simple Hook Design
– Touchscreen Control
- Three Separate Parts
– Clear Portion
– Top Lid
– Lid Support

# Dispenser/Tray

Features:
- Dispenser

– Baseplate, Camera Holder (Drop Spot) – 3 Inch Opening
- Camera

– Tilted to See Pills
– (Testing Needed For Position)
- Slide/Tray

– 1.5 Inch Extension Out
- LED

# Touchscreen Housing


Features:
- Three Part Set

– Faceplate
– Touchscreen Holder
– 5” Touchscreen
- 60 Degree Angle

# Overall Housing


Features:
- Walls
- Baseplates (3)

– Top Plate
– Drop Plate
– Base Plate
- Rubber Feet
- Connection Points

# Hardware Overview

Components:
- Total Parts ~16
Hardware Testing Done:
- Tested Motor Torque
- Motor Key Fitting, Screw Fitting, Bolt Fitting
- Parts Printed:
– | Rotating Capsule
– | Motor Holder
In Progress:
- Fabrication
- Alignment For Models
- Fixing Small Model Errors
- Supports Lid Base


To Do:
- Camera Position, Tray Piece Testing

## Design Cost Analysis

Contingencies: 30-50%

Parts: | Cost: | Parts: | Cost:
Raspberry Pi 4B | $200 | Screws/Bolts/Nuts | $7.8
Pi Cord | $8 | Cable USB | $6.12
Touchscreen | $100 | Cable HDMI | $3.00
Camera | $25 | Hinge(2) | $4.53
Stepper Motors | $22 | SD Card | $10.81
Servo Motor | $4
Ball Bearings (4) | $1 | Total Cost: | $399.26

Future Contingency Costs: >$50

# Testing and Experimentation

Hardware Testing:
- Unit testing
- What does each part do? Does it accomplish that function?
- What are some design constraints?
- Integration testing
- Do parts fit together?
- How does the system as a whole function?
Electrical testing:
- Unit testing
- Are individual components functional?
- Can we make the components behave as desired?
- Are the components a good fit to accomplish the task?
- Integration testing
- Do the parts work well together?
Software Testing:
- Unit testing
- Server communication?
- UI?
- Backend?
- Integration Testing
- Does the backend handle inputs from the front end correct?
- Does the information transfer between the server and the smart pillbox correctly?

Daniel Jacobs

# Project Plan

Stephen Fransen


# Project Plan


Stephen Fransen

# Risk Management

| Negligible | Minor | Moderate | Significant | Severe
Very Likely | 3D Printer Failure
Likely | | | | Server/Networking Issues
Possible | Motor Failure | Selected Parts are Unavailable | Broken Parts/Screens
Unlikely | | | | Design Does Not Meet Specification

Very Unlikely

Impact

Likelihood

Stephen Fransen

# Hazard Analysis

Wrong Drug Dosage: Smart pill boxes may have inaccurate dosages if users forget to double-check their input or if the machine malfunctions

Mitigation Strategy:
Keep and display a record of all medications taken and dosages.

Malfunctioning: The smart pill box may malfunction due to programming errors, hardware issues, or power outages, leading to incorrect prescriptions being dispensed.

Mitigation Strategy:
Regularly check and maintain the device to ensure it is functioning properly. Implement a redundancy system that can detect any errors and alert the user.

# Hazard Analysis

Accidental Overdose: Overdose of medication due to incorrect dosage settings or incorrect usage of the device.

Mitigation Strategy: Educate users on how to use the device correctly, including instructions on how to set the dosage, and provide an emergency contact number in case of accidental overdose. The smart pill box should be programmed to alert the user if too many doses are taken in a day.

Security and privacy risks: Data stored on the device may be accessed by unauthorized users.

Mitigation Strategy: Utilize encryption technology to protect user data from being accessed by unauthorized users and to prevent data tampering. Additionally, provide a secure login system with password protection.

# Presentation Work Disbursement

Zarek- Description, Design Constraints, Considerations, Hardware Design (I & II), Hazard Analysis

Zahra- Parts Research, Price Research , and Schematic

Stephen- Risk Management, Software Design, Project Plan, Web Application Features

Daniel – Testing, Decision Matrix, and Experimentation

# Questions?

# References:

Prescription drug statistics 2022 (singlecare.com) (https://www.singlecare.com/blog/news/prescription-drug-statistics/)

Medication overload and older Americans -Lown Institute (https://lowninstitute.org/projects/medication-overload-how-the-drive-to-prescribe-is-harming-older-americans/)

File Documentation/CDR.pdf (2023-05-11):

## Critical Design Review

## ECEN 4024: Smart Pill Box Team

Spring 2023


Report Presented by:

Zarek Rooker

Daniel Jacobs

Zahra Alnahwi

Stephen Fransen

Advisors:

Dr. Weihua Sheng, Joel Quarnstrom (GA), Su Zhidong (GA)

Electrical and Computer Engineering

Oklahoma State University

ECEN 4024 | Project SPB | Spring 2023

## Table of Contents

1. Team | 4
1.1. Team Structure | 4
1.2. Advisors | 4
2. Problem Objective | 4
3. Design Constraints | 4
3.1. Performance Constraints | 4
3.2. Economic Restraints | 5
4. Ethical Responsibilities | 5
4.1. Global | 5
4.2. Economic | 5
4.3. Societal | 6
4.4. Environmental | 6
5. Design Details | 6
5.1. Electrical | 6
5.1.1. Microcontroller/ Microprocessor | 6
5.1.2. Motors | 8
5.1.3. Camera | 10
5.1.4. Touch Screen and Speaker | 11
5.1.5. Power Supply | 12
5.1.6. Power Button | 13
5.1.7. Power Indicator: | 13
5.1.8. Power Consumption: | 14
5.1.9. Circuit Schematic Diagram: | 15
5.2. Hardware | 16
5.2.1. Introduction | 16
5.2.2. Overall Design | 16
5.2.3. Rotating Capsule | 17
5.2.4. Lid & Locking Mechanism | 18
5.2.5. Dispenser & Tray | 18
5.2.6. Touchscreen Housing | 19
5.2.7. Overall Housing | 20
5.3. Software | 20
5.3.1. Front-End | 20
5.3.2. Back-End | 21

6. Testing Strategy and Results | 21
6.1. Electrical | 21
6.2. Hardware | 21
6.3. Software | 22
6.3.1. Front-end | 22
6.3.2. Back-End | 22
7. Cost | 22
7.1. Cost Breakdown | 22
7.2. Parts List | 23
7.2.1. Electrical Parts | 23
7.2.2. Hardware Parts | 23
8. Scheduling | 24
8.1. Initial Schedule | 24
8.2. Current Schedule | 24
9. Risk Management | 24
10. Report Contributions | 25
11. References | 25

### 1. Team

### 1.1. Team Structure

- Zarek Rooker
- Role: Hardware Manager & POC
- Assignment: Hardware Design, Electronic Testing
- Zahra Alnahwi
- Role: Circuit Designer:
- Assignment: Electronic Design & Testing
- Stephen Fransen
- Role: Backend Dev
- Assignment: Software, Server Building
- Daniel Jacobs
- Role: UI Designer:
- Assignment: Software, User Interface

### 1.2. Advisors

The project is advised by Dr. Weihua Sheng and Graduate Assistants Joel Quarnstrom and Su

Zhidong. Both graduate assistants offer advice and explanation. Joel offers advice in hardware

design and testing while Su assists in electronic and software advice.

### 2. Problem Objective

The main vision of this project is to provide an efficient and safe way to manage medication for

elderly patients, especially those with cognitive decline, memory loss, and visual impairments. The

Smart Pill Box (SPB) can help them to take medication correctly and on time, reduce medication

errors, and provide a better way for caregivers to monitor the medication adherence. The SPB can

also provide a more convenient, user-friendly, and cost-effective solution compared to other existing

solutions.

### 3. Design Constraints

### 3.1. Performance Constraints

The following specifications are the main driving point for our design throughout this document.

Optional specifications are also listed below.

Specifications

1. Store medicine for 7 days and for morning, noon, and evening
2. Lock/Unlock mechanism for medication.
3. User interface with a touch screen
4. Speaker to remind the user to take medication.
5. Camera to capture images of the user taking medication.
6. Send notifications to caregivers upon completion of medication-taking.
7. Store medication data in a remote cloud server

Optional:

1. Recognize pill types and quantity through images taken by the camera (optional)
2. Support user authorization through face recognition or fingerprint (optional)

### 3.2. Economic Restraints

The design of the smart pill box should be cost-effective and accessible for customers. A hard

budget of $1000 has been allocated to research and development for our project. To keep research

and development within budget, our team aims to reduce the cost to around $500 to allow for

potential contingency costs.

### 4. Ethical Responsibilities

### 4.1. Global

Global responsibilities for a smart pill box include meeting regulatory standards, safety requirements,

and performance requirements. The pill box must ensure that it is compliant with all applicable laws

and regulations and must be certified as meeting the applicable safety and performance

requirements.

### 4.2. Economic

The economic responsibilities associated with a smart pill box are significant. It is important that the

device is affordable for those who need it. This means that the device must have a low development cost to allow for appropriate production cost. Additionally, the device must be made with high-

quality materials that will last for a long time.

### 4.3. Societal

The ethical responsibility for using these statistics is to ensure that elderly patients have access to

their medications, are aware of how to use and manage them, and can take them safely. Additionally,

the design should be intuitive and tailored to the elderly user to reduce the risk of medicine

contamination and accidental ingestion. Lastly, it is important to provide education on how to use

and manage medications, as well as the potential side effects, so that elderly patients can make the

best decisions for their health.

### 4.4. Environmental

The user should also be aware of the materials used to make their Smart Pill Box. Our Smart Pill

Boxes will be made with PLA, which is a biodegradable material. To protect the environment, the

other materials used should be either biodegradable or recyclable. In addition, the Smart Pill Box

should reduce the amount of energy used. The device should strive to utilize the lowest amount of

energy possible. This will help to reduce energy waste and protect the environment.

### 5. Design Details

### 5.1. Electrical

5.1.1.Microcontroller/ Microprocessor

When it comes to the microcontroller/ microprocessor choice, two options were considered:

Arduino and Raspberry Pi. While both are great for such projects, the Raspberry Pi would be more

suitable for this one for some reasons. Firstly, the Raspberry Pi has a superb processing power (~16

GHz) than the Arduino (~16MHz). Secondly, when it comes to data transfer, the Raspberry Pi can

transfer the data via SD Card, USB, or FTP whereas the Arduino can only do so via the flash of the

microcontroller. Thirdly, the Raspberry Pi can connect easily to the Internet with Ethernet or WiFi

while most Arduino boards do not support the Internet without extra modules. Lastly, unlike the

Arduino, the Raspberry Pi can run multiple applications at the same time. For those reasons, the Pi

would be the best choice.

Furthermore, the Raspberry Pi has many models, and each model has its pros and cons. The chosen

model is Raspberry Pi 4 Model B 2019 Quad Core 64 Bit WiFi Bluetooth (4GB)(Figure 5.1.1). Its

specifications are:

1. Broadcom BCM2711, quad-core Cortex-A72 (ARM v8) 64-bit SoC @ 1. 5GHz---

4GB LPDDR4-2400 SDRAM

2. 2.4 GHz and 5. 0 GHz IEEE 802. 11B/g/n/ac Wireless LAN, Bluetooth 5. 0,

double-true Gigabit Ethernet

3. 2 × USB 3. 0 ports, 2 x USB 2. 0 Ports---2 × micro HDMI ports supporting up to

4Kp60 video resolution

4. 2-lane MIPI DSI/CSI ports for camera and display--4-pole stereo audio and

composite video port--Micro SD card slot for loading operating system and data

storage

What distinguishes this model from others is the fast processor, more and faster RAM, dual micro

HDMI ports and the 4k output. As shown in the Circuit Schematic Diagram section, the raspberry

pi will be controlling the camera, motors, touch screen, power switch, and power indicator.


Figur.5.1.1. Raspberry Pi 4 Model B

### 5.1.2. Motors

When it comes to the motors selection, this is actually one of the challenging parts. The main goal is

to choose a strong motor that can withstand the load of the rotating capsule disk. The Stepper

motor - NEMA-17 was chosen at first (Figure 5.1.2) with its HAT (Figure 5.1.2) . A major

challenge was faced and that is the motor needs a separate power supply. To solve that, 4 solutions

were considered.

1. to use 2 separate wall plugs (1 for the Pi, the other for the motor). This was not a suitable

solution for it is not convenient to have 2 wall plugs for the same machine.

2. to use 1 wall plug and battery pack. Although this solution is better than the first, it was still

not a desired option because the goal is to use only 1 power supply to make it more

convenient for the user.

3. to use 1 AC to DC converter that has 2 outputs (1 for the Pi and the other for the motor).

Similarly to the previous solutions, this was not a desired option for the converter has a huge

size and adds more cost.

4. after more research, it was finally found that motors with low drawn current, strong enough

to handle the rotating capsule disk, and does not require a separate power supply exist. This

motor shown in (Figure 5.1.3) comes with a motor driver board that gets connected to the

Pi (does not require another power supply). Furthermore, another servo motor

(Figure 5.1.4) will be used for the locking mechanism. The servo motor does not need a

separate power supply nor a motor driver board. Both motors will be powered by the Pi.

The power consumption of both motos is shown in the Power Consumption Section below.


Figure 5.1.2. Stepper Motor NEMA with Hat


Figure 5.1.3. Stepper Motor with Driver

Figure 5.1.4. Servo Motor

### 5.1.3. Camera

One of the requirements of the project is to capture images of the user taking the medication. To

achieve that, the Raspberry Pi Camera Module 3 (Figure 5.1.5) is used. It is the latest compact

camera for the Raspberry Pi. Some of its features are:

1. Back-illuminated and stacked CMOS 12-megapixel image sensor (Sony IMX708)
2. High signal-to-noise ratio (SNR)
3. Phase Detection Autofocus (PDAF) for rapid autofocus
4. Resolution: 11.9 megapixels
5. HDR mode (up to 3 megapixel output)
6. Low power consumption (1.25W max)


Figure 5.1.5. Raspberry Pi Camera Module 3

### 5.1.4. Touch Screen and Speaker

Another requirement is to have a user interface with a touch screen and to have a speaker to remind

the user to take the medication. To achieve this, two options were considered. The first option is to

have a separate touch screen and a speaker connected to the Pi. Another option is to use a touch

screen with a built-in speaker. The second option is the chosen one for it’s more convenient and

more organized. The ELECROW Raspberry Pi Monitor 5 Inch Touchscreen, which has a built-in

speaker (Figure 5.1.6) , is the chosen solution. The features that make this a great fit are:

1. Mini Screen for Raspberry Pi: 5 inch monitor
2. Support 800*480 resolution
3. Capacitive USB Touchscreen: simply power the USB touch port to achieve touch function

and no need to install the driver

4. Support Speaker, Brightness & Volume Adjustment
5. Neat and Organized: all wires and connectors are hidden behind the screen


Figure 5.1.6. ELECROW Raspberry Pi Monitor 5 Inch Touchscreen with built-in speaker

### 5.1.5. Power Supply

For this project, it is necessary to choose a proper power supply that would be able to withstand the

loads connected to the Raspberry Pi. Two options were considered. The first is using a battery and

the other is using Official Raspberry Pi Power Supply (Figure 5.1.7). As far as using the battery, a

Battery Management System (BMS) is needed which adds more complexity and cost to the design.

Therefore, it was decided to use the Official Raspberry Pi 4 USB-C Power Supply. Its specifications

are as below:

1. 5.1 Vdc
2. 3A
3. 15.3 W

As the power consumption calculations shown below in Power Consumption Section, the chosen

power supply would be suitable.


Figure 5.1.7. Official Raspberry Pi Power Supply 5.1V 3A with USB C

### 5.1.6. Power Button

The Raspberry Pi does not come with a built-in power switch. It is not recommended to just pull the

power supply plug for the Pi because that might cause the SD card and the file system to be

corrupted. The Raspberry Pi could be safely shut down via a software command. But to make it

easier for the user, a power button will be used. By shutting down the Raspberry Pi, it is meant to

put it in “Halt State” in which the Pi still uses very little power. The purpose of the power button is

to put the Pi in the halt state and to wake the Pi from it. Moreover, the power supply could be safely

disconnected once the Pi is on the Halt State. What is needed to make the power button work are:

SPST NO switch, wires, and writing the code. To understand how the wake function works, simply

by shorting pin 5 (SCL) pin with any GND pin wakes the Pi from the Halt State. The same pins will

be used to shut it down. A script is written to listen for a button press to shut down the Pi. Edge

detection method is used for this process. Basically, the Pi listens for an interrupt, which is the

change in state from LOW to HIGH or HIGH to LOW. A method called “wait_for_edge” is used

to block the execution of the script until an interrupt is detected. The GPIO pin is set up to

shutdown the Pi once a Falling edge is detected. The power Switch shown in (Figure 5.1.8).


Figure 5.1.8. Push Button Switch

### 5.1.7. Power Indicator:

An LED in series with a resistor is connected to 1 GPIO pin and 1 GND pin that will indicate

whether or not the Pi is on.

### 5.1.8. Power Consumption:

In this section, the power consumption for each part is calculated based on the data from datasheets of the parts. The table below shows the summary for that. As mentioned above in the Component Section The Official Raspberry Pi 4 USB-C Power Supply has an input of 5.1V, rated current of 3A, and max power consumption of 15.3W. It can be seen in the below table that the sum of the max drawn current and power consumption of each component did not exceed the limits.

Part | Voltage | Voltage Source | Max Drawn Current | Max Power Consumption
1- Raspberry Pi | 5.1 V | Official USB-C power supply | 0.6A - 1.2 A | 3.06W - 6.375 W
2- Camera | 3.3 V | Raspberry Pi (Camera Connectors available) | 0.2A - 0.25A | 0.66W - 0.825 W
3- Touch Screen | 5 V | Raspberry Pi (USB) | 0.5A | 2.5 W
4- Motor (Stepper Motor + Driver) | 5 V | Motor Driver *Driver is power by Raspberry Pi (GPIO pins)* | 0.24 A | 1.2 W
5- Motor (Servo Motor) | 5 V | Raspberry Pi | 0.1A - 0.36A | 0.5W - 1.8W
6- LED + Resistor | 3.3 V | Raspberry Pi GPIO pins | 0.002A -0.01A | 0.0066W -0.033W
Total Estimated Max Power Consumption | 12.733W
Total Estimated Max Drawn Current | 2.56A


### 5.1.9. Circuit Schematic Diagram:

To make the circuit schematic diagram, Multisim software is used. Most of the parts in this project

(Raspberry Pi, Motors, Touch Screen, Camera) cannot be found in Multisim. Therefore, using the

Component Wizard tool in Multisim, a model for each component is created.

Pins Layout:

### 5.2. Hardware

### 5.2.1. Introduction

The hardware components have multiple different sections that make up its design. We must

consider the compartments that hold the pills, the locking mechanism, the overall housing design,

and how to properly secure the device. This section will be broken down into five main sections: the

Rotating Capsule Piece, Lid, Dispenser, Touchscreen Housing, and overall Housing. Each

component is designed to be intuitive and user-friendly, utilizing materials that are both aesthetically

pleasing and durable to ensure that the device is secure and stable. Furthermore, the design of the

Smart Pill Box ensures that the medication is easily accessible and can be quickly refilled when

necessary.

### 5.2.2. Overall Design


Figure 5.2.1: Overall Design

The overall design of the device can be seen in Figure 5.2.1. We will break down all the major

components that make up the overall design, with a focus on visibility, easy loading, accessibility,

and a 7-day supply. The dimensions of the design are 10” x 4” x 8” and the estimated weight is 3.283

lb. With this size, we can store more than 5 pills in one compartment, and loading is made easy with a lid that opens for mass loading. A touchscreen is featured on the front for user friendliness and the

dispenser is clearly shown with an intuitive tray for the user to get pills from.

### 5.2.3. Rotating Capsule


Figure 5.2.3: Rotating Capsule Piece (Bottom View)

The requirement for a locking mechanism pushed us to a design like the rotating capsule (Figure

5.2.2). The rotating capsule piece has 22 compartments for a 7-day supply to be held. The piece will

sit on a stepper motor that will provide enough torque to rotate the device. The each cut out on the

piece holds one time for taking medication (ex. Monday at 8 am). The device will also include a

physical display of the day that it is on.


Figure 5.2.4: Motor Holder and Key

To allow for adjustments we are including a motor holder and motor key. Both pieces allow us to

verify the fit of the motor and the fit of the axle. This allows for easy adjustment and reduces 3D

print times. As we can see in Figure 6.2.4 the motor holder is the gray piece and will include cutouts

for the wires of the stepper motor to come out. It also has 4 screw holes to allow the drop plate to

connect. The motor key is the black piece and fits into the rotating capsule piece (Figure 6.2.3).

These pieces have already been printed but are already subject to change. Specifically, they will be

adjusted to host ball bearings.

### 5.2.4. Lid & Locking Mechanism


Figure 5.2.4: Lid and Locking Mechanism

This lid mechanism is designed with a three-part system (Figure 5.2.4, Left). The first part is the top

piece which is the outside of the box. The second part is a clear portion, which provides a clear view

of the contents inside smart pill box. The third part is at the bottom plate of the lid and will allow

for a flush finish that keeps all the components of the lid secured. The top lid is made of durable

material and the lid support ensures that the lid remains in place. The locking mechanism is a simple

hook design, which allows the user to easily lock and unlock the mechanism (Figure 5.2.4, Right).

This will be controlled by the touchscreen, which allows for easy access to the locking mechanism.

This locking mechanism is the perfect solution for securing the pills and keeping them safe.

### 5.2.5. Dispenser & Tray


Figure 5.2.5: Dispenser & Tray


The dispenser of the Smart Pill Box will have multiple features (Figure 5.2.5, Left). It will be made

of a baseplate and camera holder, and the opening will be 3 inches wide, big enough for most hand

sizes to fit into. There will also be a tray that allows for the medicine to be removed and cleaned

more easily (Figure 5.2.5, Middle). Inside the dispenser, a camera will be housed to take before and

after pictures of the medicine being taken from the compartment. The camera will be held and

secured in the camera holder (Figure 5.2.5, Right), and an LED will provide better visibility and

clarity of where the medicine is dispensed.

### 5.2.6. Touchscreen Housing


Figure 5.2.6: Touchscreen Housing Parts


The touchscreen housing (Right) also has three components: a faceplate (Left), a touchscreen holder

(Middle), and a 5” touchscreen. The design was created to introduce a finishing touch to the holder.

The faceplate will be placed on the front of the holder to present a flush finish with no screw holes

visible. The 5” touchscreen will be securely inserted into the holder and will support all the necessary

connectivity. The connections will all be hidden at the back and out of view from the user. The touchscreen will be set at a 60-degree angle to enable the user to clearly see the device even if it is at

waist height. The overall holder design will connect to the overall housing to provide a finished look.

### 5.2.7. Overall Housing


Figure 5.2.7: Housing Walls


Figure 5.2.8: Top Plate, Drop Plate, and Bottom Plate

The overall housing consists of the walls (Figure 5.2.7) and baseplates (Figure 5.2.8). The wall of the design is very simple and will have a cutout to allow for power to connect to the system. The baseplates will have three components the top plate, drop plate, and baseplate. The top plate will be flush with the rotating capsule and will be visible when the lid is open. The drop plate is where the pills will be dispensed and will hold all the pills on it. It will also hold the place the servo will be used to lock the device. Finally, the baseplate is the bottom of the project and will have rubber feet to secure the device onto any surface. The two components will be connected by screws, bolts, and nuts to allow for an accurate finish.

### 5.3. Software

### 5.3.1. Front-End

The front-end will consist of two access points. The first is the screen on the smart pillbox accessed by the user. The second is through a webserver accessed by the user’s caregiver. We are designing these interfaces using HTML, CSS, and Javascript. Then, for the GUI on the smart pillbox, we will use Electron to package the code into an offline portable app that runs on the raspberry pi. For the webserver, we will host it on a remote server that will serve the webpage to the caregivers.

The functionality available to the on the pillbox includes dispensing medications at set times, refilling medications, taking pictures of dispensed medications, alerting the user that it is time to take medications, and alerting the caregiver of missed doses. All of this will be done through the raspberry pi within the box. There will be a touch screen for the user to see a list of medications, see times that are scheduled, and input a code to receive medicine.

On the caregiver side of the front-end, the website will have a secure login. On the main page, there will be a list of patients under their care. Once they click on a patient, they will have a list of medications and times similar to what will be displayed on the user’s pillbox. One important feature will be receiving an image of all the pills dispense recently and an alert if there were none dispensed. The caregivers will also have access to set up medications and times to take them.

### 5.3.2. Back-End

For the backend, we decided to move to a remote server as this will allow us to send notifications easier and serve as a more unified experience if the smart pillbox is produced en masse. The backend will consist of a webapp made using Flask that will be hosted on a server using a combination of Gunicorn and NGINX. We chose Flask primarily because we had used previously in Embedded Systems and are confident we can deliver on all of the requirements. The Flask will be accompanied by the various HTML, CSS, and JS files that are required to get the webapp functioning. We chose Gunicorn and NGINX primarily because the Flask documentation heavily recommends using this combination. Gunicorn is a WSGI server for the Flask application, and we are using NGINX to serve the HTTP calls for increased security and efficiency.

Additionally, we will be using PostgreSQL as our database. This will store usernames, passwords, medication lists, user roles (caregiver/patient), and any camera captures. This will be secured using hash maps to ensure confidential information is leaked.

### 6. Testing Strategy and Results

### 6.1. Electrical

To test the parts on the Pi, a code is needed to be written to it. The parts have not arrived yet except

the camera module. Luckily, one of the team members has a Raspberry Pi and a stepper motor

which allowed the team to test them. The first test of the Raspberry Pi, stepper, and camera was

successful. The plan is to test each component separately with the Pi, and then to connect them

together. After connecting each part separately, the drawn current from the part and the power

consumption will be measured to compare it with the power consumption calculations done to

make sure the Pi does not get overloaded.

### 6.2. Hardware

Testing the hardware for a smart pill box is an important part of the manufacturing process. The hardware must meet certain standards to ensure the device is safe and reliable. This usually involves testing the connections of the components, checking for any potential malfunctions, and testing the overall design of the device. Additionally, the hardware must be tested for its durability and ability to withstand any potential external forces. Through these tests, we can ensure that the smart pill box is safe and reliable for its intended purpose.


Figure 6.2.1: 3D Printed Rotary Capsule

With 3D Printed parts connections always seem to be a problem. We have already tested the screw fittings, bolt fittings, and the size of the overall model. Figure 6.2.1 shows the size of the rotating capsule. The image depicts the number of pills that can fit in each slot, and it is easily over 5 pills.

Initial hardware testing we have already conducted include testing the motor torque to see if it can support the rotating capsule piece. The test was successful, and we have already learned how to increase performance. The biggest solution is to reduce the friction coefficient. This can be done by having a lighter model, ball bearings or ball rollers, and potentially a different material with a lower friction coefficient.

### 6.3. Software

### 6.3.1. Front-end

Front-end testing will consist of making sure the flow of the program is consistent with intended design and is also responsive. For example, ensuring the touch screen works with the interface is important because that is our main way of interacting with the device. Other parts we will test are the speakers going off at the correct times and user logins being accessible.

### 6.3.2. Back-End

Back-end testing will ensure that data flows properly and consistently between the raspberry pi, the webserver, and the caregiver. Some tests we will implement are database entries showing up after sent from the pi and image receiving on the caregiver’s end.

### 7. Cost

### 7.1. Cost Breakdown

The device has parts cost of $399. The break down is shown in the table below:

Parts: | Cost: | Parts: | Cost:
Raspberry Pi 4B | $200 | Screws/Bolts/Nuts | $7.8
Pi Cord | $8 | Cable USB | $6.12
Touchscreen | $100 | Cable HDMI | $3.00
Camera | $25 | Hinge(2) | $4.53
Stepper Motors | $22 | SD Card | $10.81
Servo Motor | $4
Ball Bearings (4) | $1 | Total Cost: | $399.26

Future Contingency Costs: >$50

Touchscreen and Pi make up 75% of cost

Production cost given purchases in bulk and utilizing any vendor. ~$250

### 7.2. Parts List

### 7.2.1. Electrical Parts

Part Description | Part Name | Price | Supplier
Microcontroller | Raspberry pi 4 Model B | $ 149 | Amazon
Touchscreen | ELECROW Raspberry Pi Monitor 5 Inch touchscreen | $61.99 | Amazon
Camera | Raspberry Pi Camera Module 3 | $25 | Cana kit
Motor + Driver | Stepper Motor + ULN2003 Driver Board | $14.99 | Amazon
Motor | SG90C 360 Degree Micro Servo | $4.00 | Mouser
Power Supply | Raspberry Pi 4 Model B Official PSU, USB-C | $7.98 | Amazon
Memory | Memory Cards 8GB UHS Class 4 MicroSD Card WD/SD | $9.56 | Mouser
Power Switch | Push Button Switch | $0 | -
Power Indicator | LED | $0 | -
Resistor | Resistor | $0 | -

### 7.2.2. Hardware Parts

Part Description | Part Name | Price | Supplier
Ball Bearings | 608-2RS-W/CHEVRONSRI2 | $1.00 | Digi-key
Screws | 36-9900-ND | $0.12 | Digi-key
Screws | 36-9901-ND | $0.12 | Digi-key
Bolts | 7235-3-ND | $0.10 | Digi-key
Hdmi-Micro | 2648-RPIHDMIADAPTER-ND | $3.00 | Digi-key
USB | 2671-USB3.0AMF-1FT-ND | $6.12 | Digi-key

Hinges | 2419-237.1-30-30-A-ND | $4.53 | Digi-key

### 8. Scheduling

Attached below are the initial and current schedules for the project. We were backed up by server researching problems and copious printing problems, but now that our design is close to finalization, the remainder of our time will predominantly testing the final design fitting and software.

### 8.1. Initial Schedule


### 8.2. Current Schedule


### 9. Risk Management

The table below shows our risk matrix, which tracks the likelihood and impact that potential problems might have along the course of this project. The most problematic circumstance that we foresee is general server/networking issues. We could have difficulty accessing the webpage remotely during our demonstration or otherwise. Hosting public webpages is a topic that we have not done before this project. We could also run into problems with the campus networking as we have had difficulties using it in the past.

Design Does Not Meet Specification: at this point in the project, we have every required part of the SPB covered. However, there is still room for plans to fall through leaving us without some of the required functionality that was asked of the team.

Selected Parts are Unavailable: This event is possible because some of the parts needed are niche or in high demand. However, in electronics, there are usually several alternatives, so it would not pose a significant risk to the project.

Broken Parts: Broken parts would delay the implementation and testing of the affected parts until we can get replacements. The impact is moderate because it would only delay us, and the likelihood is “possible” because shipping can be rough on components sometimes.

Parts Arrive Late: This would have a similar impact to broken parts because it would delay our progress. However, it is unlikely because shipping methods are generally predictable and tracking can keep us updated on expected arrival times.

IMPACT

LIKELIHOOD

Negligible | Minor | Moderate | Significant | Severe

Very
Likely

3D Printer
Failure
Likely | Server/Network
ing Issues
Possible | Motor Failure | Selected Parts
are Unavailable | Broken Parts/Screens
| | Not Meet Specification
Unlikely | Parts Arrive Late | Design Does

Very
Unlikely

### 10. Report Contributions

Zarek: Problem Objective, Constraints & Ethics, Hardware Design, Hardware Testing

Daniel: Software design, Software testing, Risk Management

Zahra: Electrical, Electrical test, Power Consumption, Circuit Schematic, Parts Price

Stephen: Scheduling, Risk Management, Back-End Software, Formatting

### 11. References

Raspberry pi or Arduino – when to choose which? Leo Rover Blog. (n.d.). Retrieved March 10, 2023, from https://www.leorover.tech/post/raspberry-pi-or-arduino-when-to-choose-which#:~:text=Arduino%20is%20an%20electronic%20board,monitoring%20weather%2 0and%20many%20others

Cdaviddav. (2021, May 7). Raspberry Pi vs Arduino comparison. DIYI0T. Retrieved March 10, 2023, from https://diyi0t.com/raspberry-pi-vs-arduino-comparison/

Piltch, A. (2020, June 2). Raspberry pi 4: Review, buying guide and how to use. Tom's Hardware. Retrieved March 10, 2023, from https://www.tomshardware.com/reviews/raspberry-pi-4

Raspberry pi camera module 3. CanaKit. (n.d.). Retrieved March 10, 2023, from https://www.canakit.com/raspberry-pi-camera-module-3.html?defpid=4836

Raspberry pi documentation. Raspberry Pi hardware. (n.d.). Retrieved March 10, 2023, from https://www.raspberrypi.com/documentation/computers/raspberry-pi.html#power-supply

Galt, J. (2020, November 25). How to add a power button to your Raspberry Pi. Howchoo. Retrieved March 10, 2023, from https://howchoo.com/g/mwnlytk3zmm/how-to-add-a-power-button-to-your-raspberrypi?utm_source=youtube&utm_medium=referral&utm_campaign=power-button-video&utm_content=description

Amazon.com: Raspberry Pi 4 Model B official PSU, USB-C, 5.1V, 3A, US ... (n.d.). Retrieved March 11, 2023, from https://www.amazon.com/Raspberry-Model-Official-SC0218-Accessory/dp/B07W8XHMJZ

Raspberry pi documentation. Raspberry Pi hardware. (n.d.). Retrieved March 10, 2023, from https://www.raspberrypi.com/documentation/computers/raspberry-pi.html#power-supply

Servo Motor Micro SG90. ProtoSupplies. (2023, January 24). Retrieved March 10, 2023, from https://protosupplies.com/product/servo-motor-micro-sg90/

SAVAGE, A. R. T. H. U. R. D. E. K. K. E. R. (2016). DP. Amazon. Retrieved March 10, 2023, from https://www.amazon.com/dp/B08343QX67/ref=emc_b_5_t

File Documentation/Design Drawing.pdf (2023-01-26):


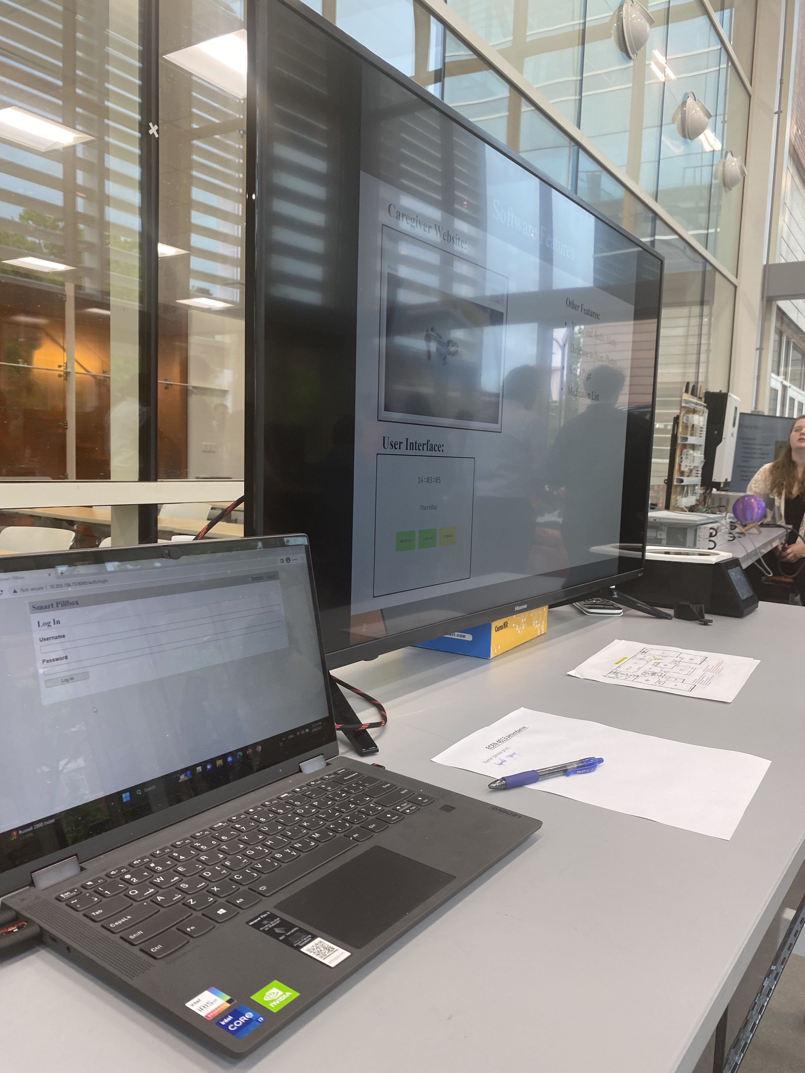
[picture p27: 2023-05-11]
Photos_Videos/70439712167__2AE94FB8-84BF-4ECB-8D14-33F2C0205F67.jpg

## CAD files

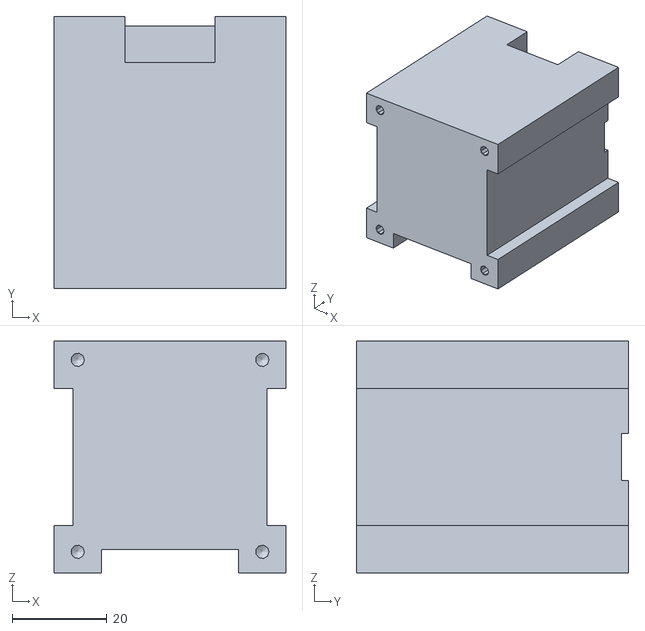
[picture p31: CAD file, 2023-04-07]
3D Models/All/Motor_Holder.stl
49.0 x 57.5 x 49.0

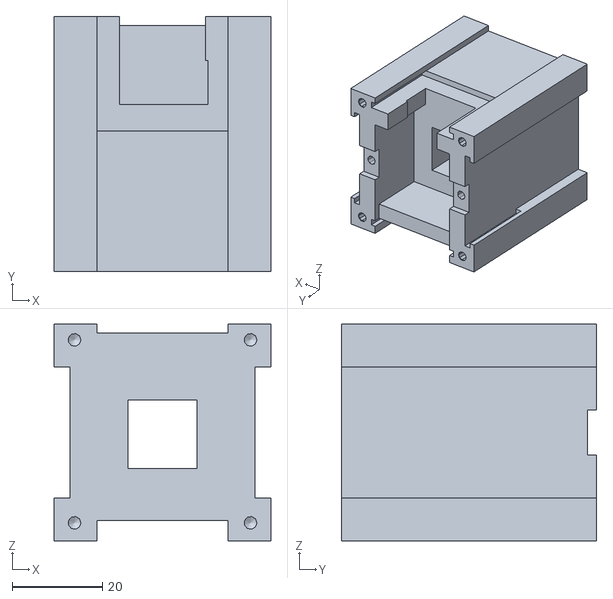
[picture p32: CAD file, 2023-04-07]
3D Models/All/Motor_Holder - Copy.stl
48.0 x 56.5 x 48.0

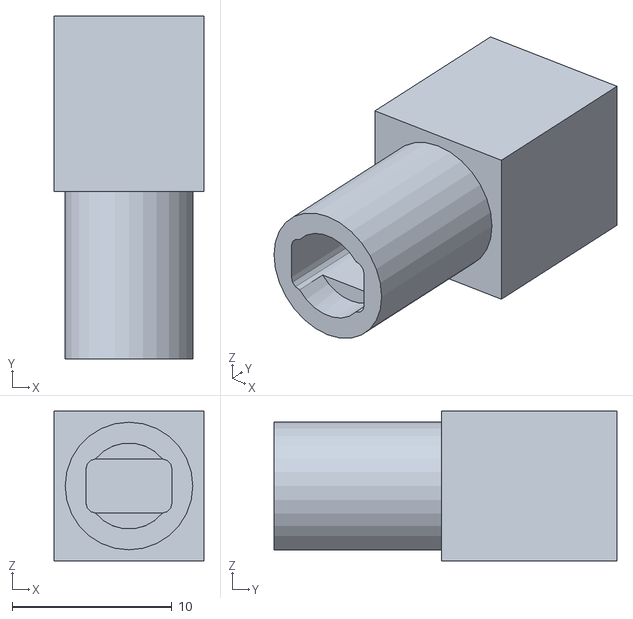
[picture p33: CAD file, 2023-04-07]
3D Models/All/Motor_Key_Bearing_3_4.stl
9.40 x 21.5 x 9.40

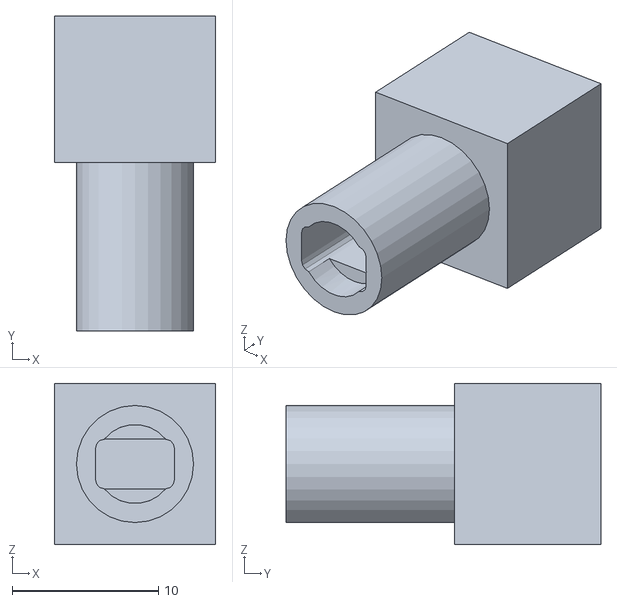
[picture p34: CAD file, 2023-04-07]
3D Models/All/Motor_Key_Bearing_2.stl
11.0 x 21.5 x 11.0

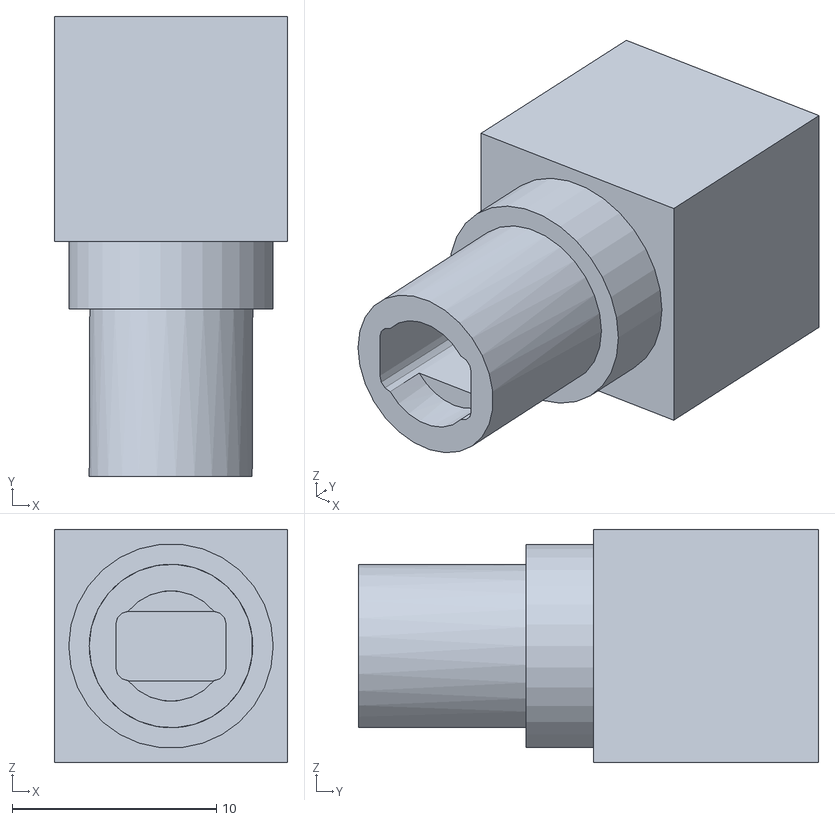
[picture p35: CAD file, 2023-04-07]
3D Models/All/Motor_Key_Bearing_2_2.stl
11.4 x 22.5 x 11.4

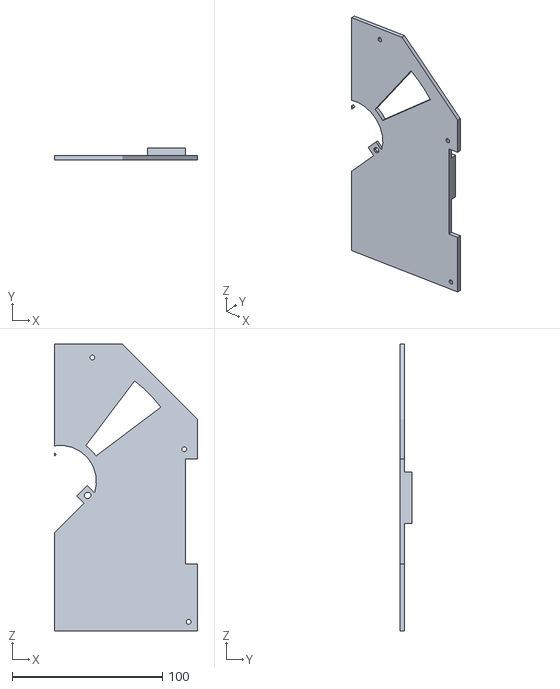
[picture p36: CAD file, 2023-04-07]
3D Models/All/Drop_Plate - Copy.5 (2).stl
95.6 x 8.00 x 191.2

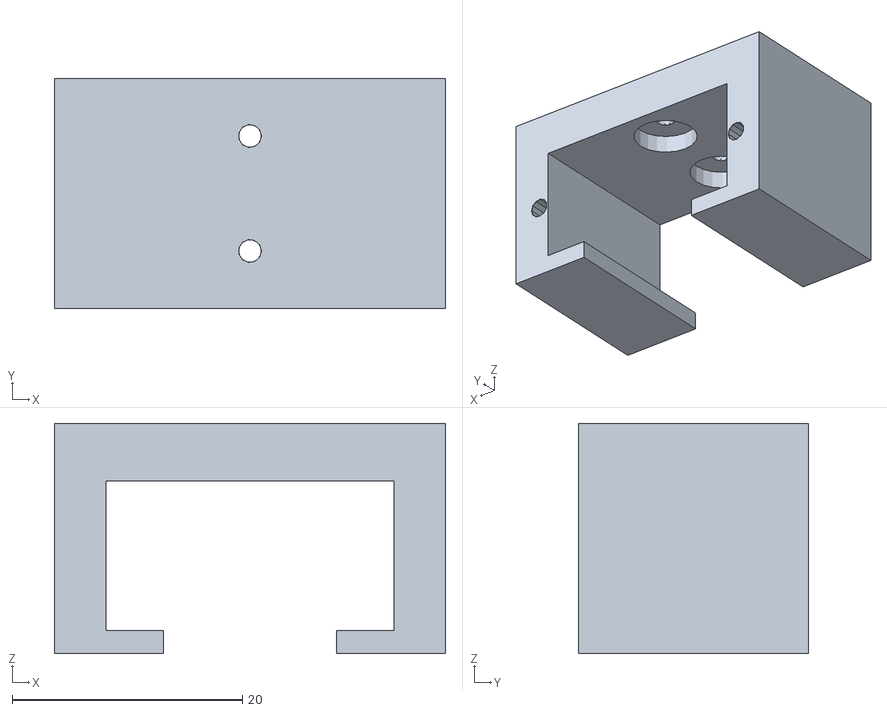
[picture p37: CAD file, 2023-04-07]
3D Models/All/Servo Holder.stl
34.0 x 20.0 x 20.0

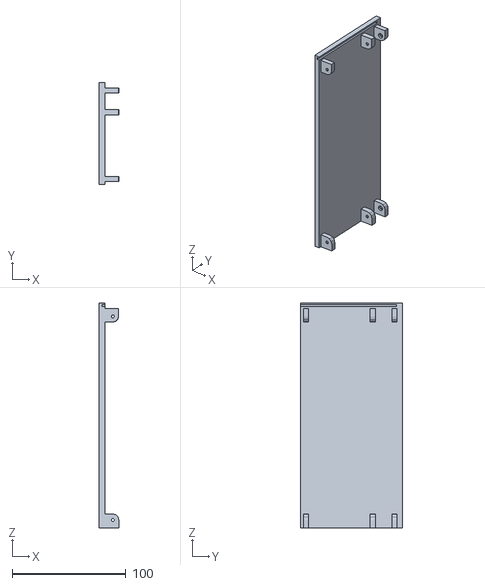
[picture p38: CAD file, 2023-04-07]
3D Models/All/Box_Walls_2 - Left Wall.stl
17.4 x 89.6 x 198.2

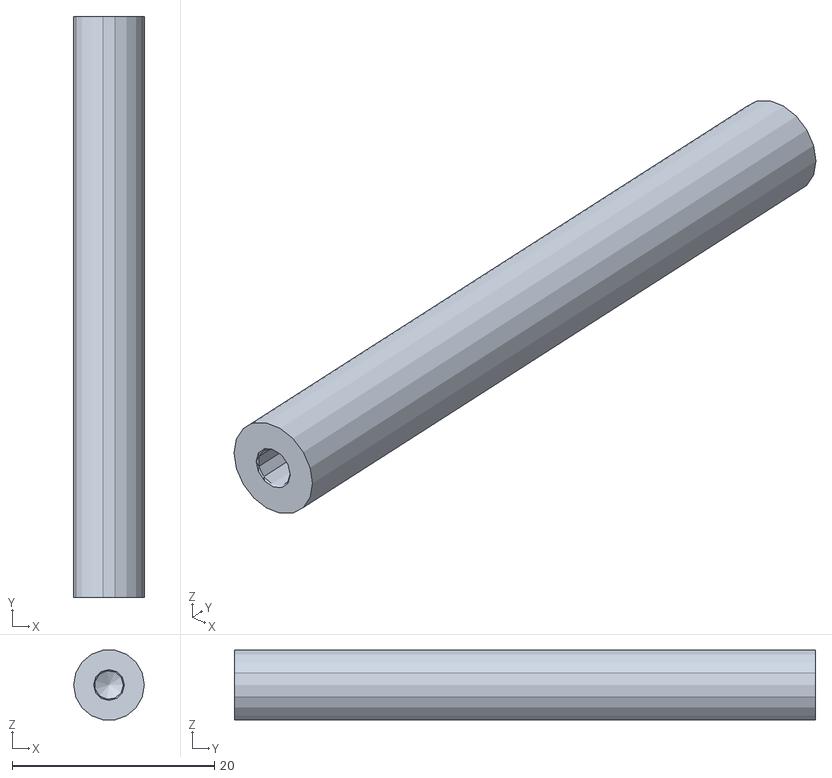
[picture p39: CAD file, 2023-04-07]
3D Models/All/Connectors.stl
7.00 x 57.5 x 6.89

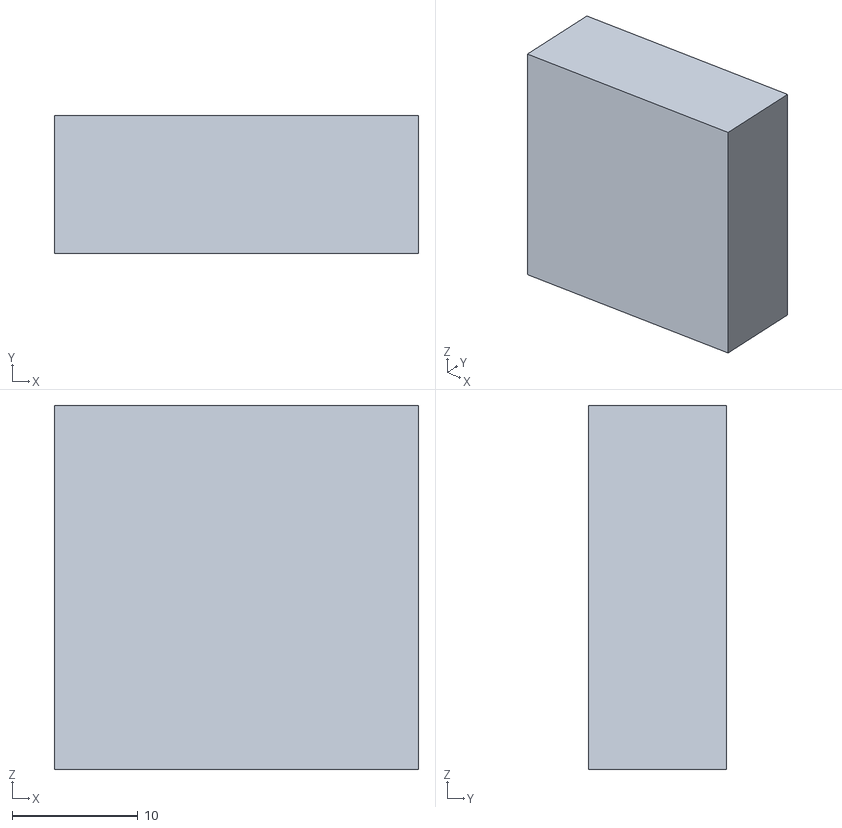
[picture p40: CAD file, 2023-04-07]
3D Models/All/Motor_Key - Copy.stl
29.0 x 11.0 x 29.0

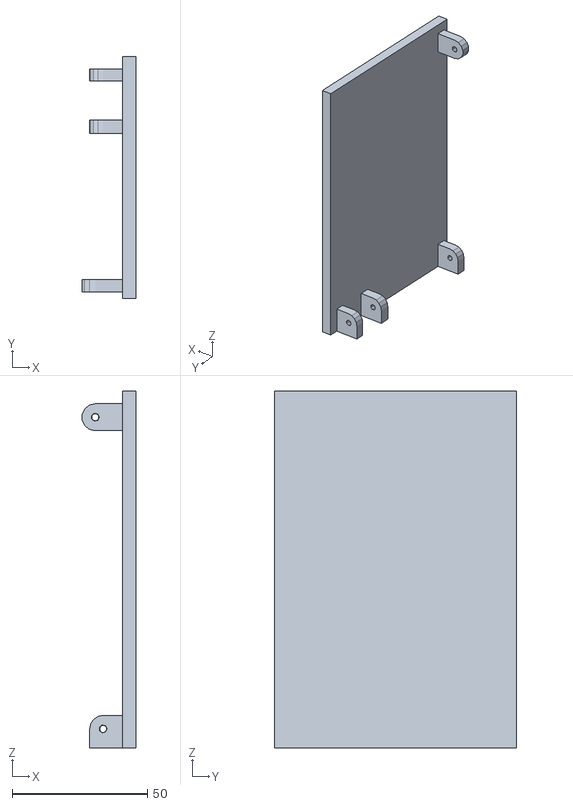
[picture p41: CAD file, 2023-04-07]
3D Models/All/Box_Walls_2 - Right Wall.stl
19.9 x 89.6 x 132.0

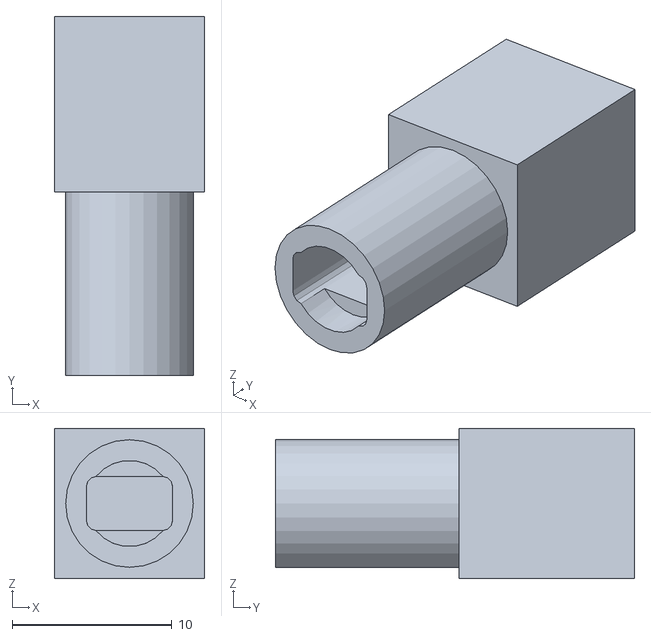
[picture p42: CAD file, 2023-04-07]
3D Models/All/Motor_Key_Bearing_3.stl
9.40 x 22.5 x 9.40

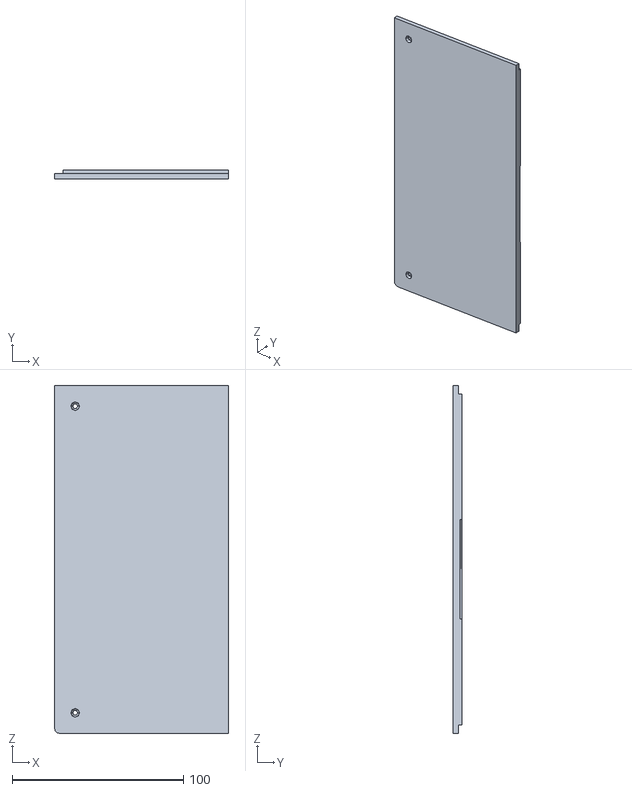
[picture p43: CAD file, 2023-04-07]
3D Models/All/Base_Plate_2_Solo_Up.5_L.stl
101.6 x 5.00 x 203.2

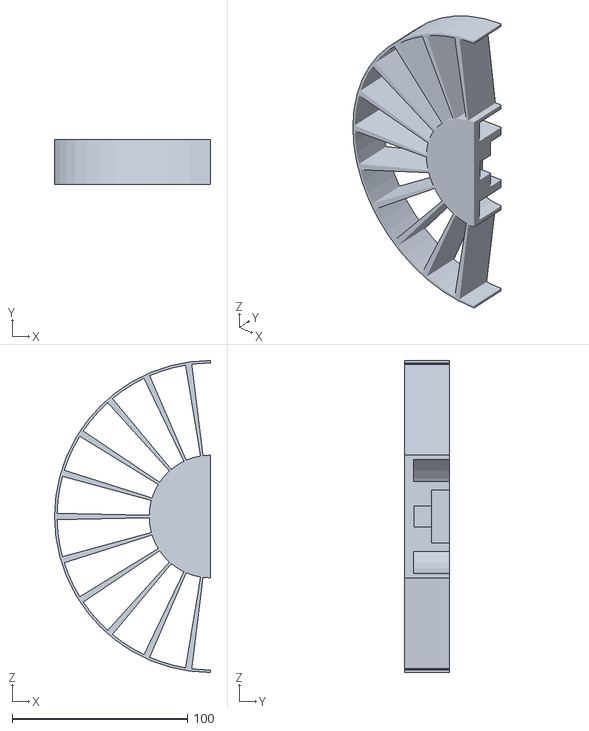
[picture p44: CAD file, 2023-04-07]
3D Models/All/Capsule_Design_Final_.5.stl
88.9 x 25.4 x 177.8

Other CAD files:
3D Models/All/Box_Walls__ Left Wall.stl
3D Models/All/Camera Angle.stl
3D Models/All/Box_Walls_2 - Opening.stl
3D Models/All/Base_Plate_2_Solo_Up.5_R.stl
3D Models/All/Adjustments.ipt
3D Models/All/Adjustments.stl
3D Models/All/Ball Bearing Inside Mechanics.iam
3D Models/All/Ball_Bearing_Holder.ipt
3D Models/All/Ball_Bearing_Holder.stl
3D Models/All/Ball_Bearing_Holder_Assembly.iam
3D Models/All/Ball_Bearing_Holder_Test.ipt
3D Models/All/Ball_Bearing_Mock_8_22_7mm.ipt
3D Models/All/Base_Plate&DropPlate.iam
3D Models/All/Base_Plate_2.ipt
3D Models/All/Base_Plate_2_Solo.ipt
3D Models/All/Base_Plate_2_Solo_Up.5.ipt
3D Models/All/Base_Plate_2_Solo_Up.ipt
3D Models/All/Base_Plate_2_With Camera.ipt
3D Models/All/Base_Plate_Assembly.iam
3D Models/All/Box Walls + Top Lid.iam
3D Models/All/Box_Walls_2 - Opening.ipt
3D Models/All/Box_Walls_2 - Right Wall.ipt
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

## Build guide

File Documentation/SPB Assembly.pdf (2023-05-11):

## How to Assemble the Smart Pill Box

Introduction:
The Smart Pill Box (SPB) is a semester long project dedicated to providing an efficient and safe way to manage medication for elderly patients, especially those with cognitive decline, memory loss, and visual impairments. These instructions will show you how to assemble and replace your features inside the Smart Pill Box. The steps that follow are intended for people with basic soldering skills, 3D Modeling experience, and electronics skills as inexperience can result in a ruined Smart Pill Box. Assembling the SPB usually takes 30-60 minutes. Following the instructions correctly can save time as it focuses on disassembly, repair, reassembling, and troubleshooting.

Parts and Tools:
The Smart Pill Box can easily be assembled with the basic parts and the basic tools needed for the assembly. Spare parts are provided and can be reprinted with the provided Gcode files. If reprinted parts are required, follow the same guide for reassembly.
- 3D Printer
- SPB Parts
- Prying Tools
- Screwdrivers
- Soldering kit (solder, soldering tool, desoldering tools, flux)

Precautionary information
Throughout these instructions, precautionary information will be displayed. These are important as they will protect your health and the usability of your controller. The precautionary information will appear as:
Precautionary Sign | Meaning
Note: | A note provides information that can be helpful
NOTICE: | A notice precaution indicated that there is a risk of damaging the controller.
CAUTION: | A caution statement indicates an action can result in minor injury to the user or damage to a component within the controller.
WARNING: | A warning statement indicates an action can result in serious injury to the user.

Disassembling the Smart Pill Box

To start, you first must disassemble the SPB to get to the electronics where our motor controllers are connected. This section will teach you how to safely disassemble the SPB without causing any more damage.

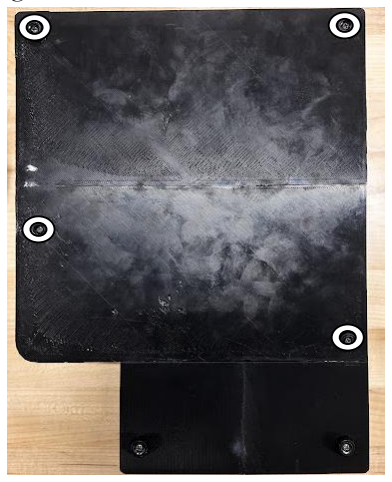
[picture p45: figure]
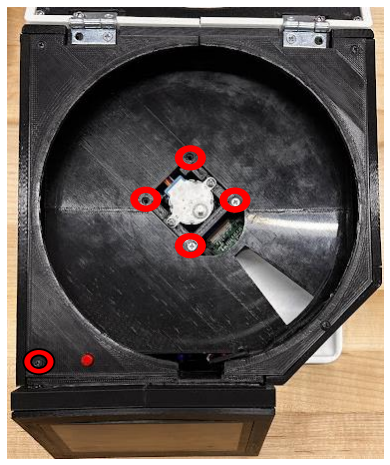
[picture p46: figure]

Figure 1 (Removing screws from Baseplate) | Figure 2 (Removing screws from Top & Drop Plate)

NOTICE: Failure to unplug the SPB can result in damage to the Raspberry Pi completely ruining the device.

1. Unplug the Smart Pill Box.
2. Remove the tray and rotating capsule.
3. Turn the Smart Pill Box over where the baseplate is facing upward.
4. Remove the screws from the bottom (baseplate) of the device.

Note: Figure 1 displays in white where the screws should be removed from. It is good practice to

place screws in a safe place to avoid losing them.
5. Carefully turn the SPB over back to the original position
6. Unscrew the five screws on the top of the Smart Pill Box that hold the drop plate in place.

Note: Figure 2 displays in red which screws need to be removed.
7. Carefully separate the top of the device from the baseplate.

Note: The board will seem stuck. Push the top walls back then pull up to avoid a screw location.
8. Place the top portion of the device to the left of the baseplate.
9. Make appropriate troubleshooting fixes if needed.

This portion was dedicated to quick access to the inside electronics of the Smart Pill Box. If further

disassembly is required continue with this guide.

Removing the Touchscreen Housing

Now that we have removed all other components, we can focus on completely disassembling the Smart Pill Box. This section will teach you which components to remove and how to protect our device in the process.

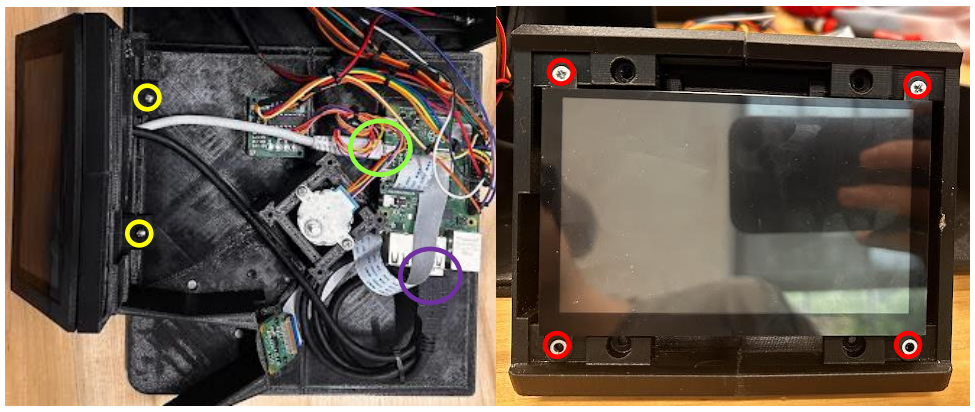
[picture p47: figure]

Figure 3 (Removing Screws for Touchscreen) | Figure 4 (Connections to desolder)

NOTICE: Unplugging the USB and HDMI connections from the touchscreen is very difficult and can cause damage to the ports. Be very careful to avoid twisting or turning these cords. Avoid damage by disconnecting from the Raspberry Pi first.

1. Unplug the micro-HDMI cord.

Note: Figure 3 shows the location (in green) where the cord should be unplugged.
2. Remove the USB connection.

Note: Figure 3 shows the location (in purple) where the cord should be unplugged.
3. Unscrew the two screws holding the touchscreen housing to the baseplate.

Note: Figure 3 displays the location of the screws for removal in yellow.
4. Carefully separate the touchscreen housing from the baseplate.
5. Set baseplate aside for future disassembly.
6. Use a pry tool to remove the faceplate from the touchscreen.
7. Remove the two screws holding the touchscreen into place.

Note: Figure 4 displays the location of the screws for removal in red.
8. Carefully pull out the touchscreen from the housing.
9. Unplug the USB and Micro USB if needed.

Unplugging the Raspberry Pi Connections

Now we can look at the removal of components from the Baseplate. This section will teach you how to disconnect the cables from the servo motor, push buttons, stepper motor, and camera.

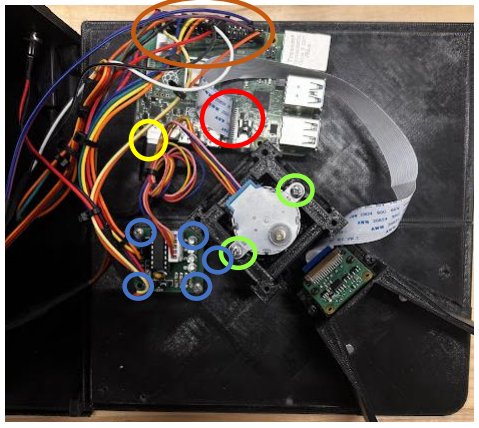
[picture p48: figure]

Figure 5 (Flush Finished Connection)

1. Unplug the USB-C extension cable.

Note: Figure 5 displays the location of the USB-C in yellow
2. Remove the camera cable by carefully lifting the gray tab.

Note: Figure 5 shows the location in red
3. Identify all contacts properly line up with the circuit board.
4. Unscrew the screws of the Stepper Motor

Note: Figure 5 shows the screws for removal in green
5. Remove the screws that hold the motor driver in place.

Note: Shown in blue in Figure 5
6. Unplug the motor driver from the Raspberry Pi.
7. Remove the other remaining connections from the Raspberry Pi.

Note: Shown in Figure 5 in orange. Appendix A displays the corresponding pinouts of each

component.
8. Unscrew the Raspberry Pi from the baseplate.

The Raspberry Pi should now be completely cleaned of any wires and removed from the baseplate. The disassembly of the top portion will now be shown, specifically the lid and walls.

Disassembling the Servo and Lid

Disassembly for the lid is rather simple. This section will teach you how to do that and make sure everything in the SPB is properly disassembled.

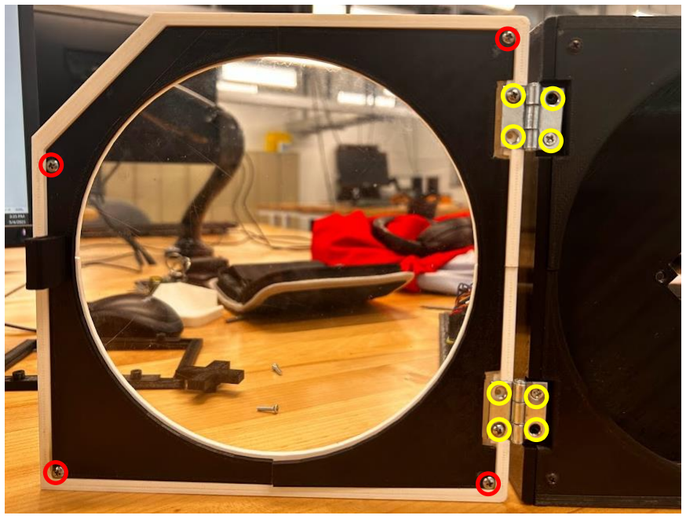
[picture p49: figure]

Figure 8 (Taking the lid apart)

1. Lift the lid until it is open.
2. Remove the screws from the hinges.
Note: Figure 8 shows where the screw needs to be removed in red
3. Unscrew the 4 other screws.
Note: Figure 8 shows where the screw needs to be removed in yellow
4. Pull lid apart as needed.

The lid should now be completely separated. For further disassembly continue.

Disassembling the Servo and Lid

Now the baseplate has been completely disassembled we can focus on disassembling the top component. This section will teach you how to do that and make sure everything in the SPB is properly disassembled.

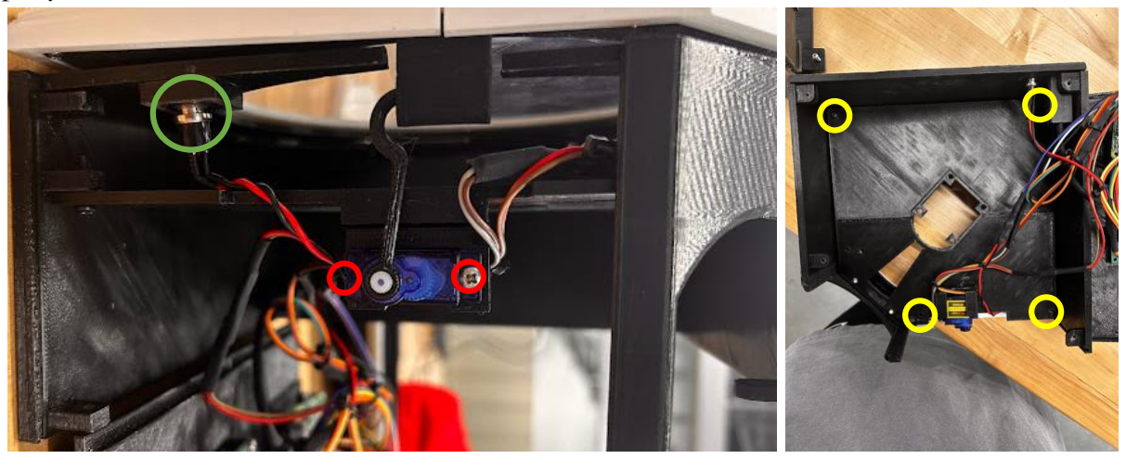
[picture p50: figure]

Figure 6 (Servo and Button Removal) | Figure 7 (Connections for walls)
1. Remove the hook from the servo motor.
2. Unscrew the servo motor.
Note: Figure 6 shows where the screw needs to be removed in red
3. Remove the servo from the holder.
4. Unscrew the holder from the drop plate and set aside.
5. Remove the Push Button.
Note: Figure 6 shows the location in green.
6. Remove the LEDs from their location.
7. Place the box where the drop plate is facing down. (Figure 7)
8. Unscrew the screws connecting the drop plate to the walls. Note: Figure 7 shows the location in yellow. Note the USB-C converter blocks the location of one screw. A longer screwdriver is recommended.
9. Turn box back over.
10. Remove remaining screws keeping the top plate connected to the walls.

The box should be disassembled now, and the plates should be separated from the walls. To create fixes for any component, follow the disassembly guide for help. Disassemble anymore components as needed for the final

Conclusion

Congratulations! You have completely disassembled the Smart Pill Box. For any more information not given look at the provided GitHub or photos provided. Good job.

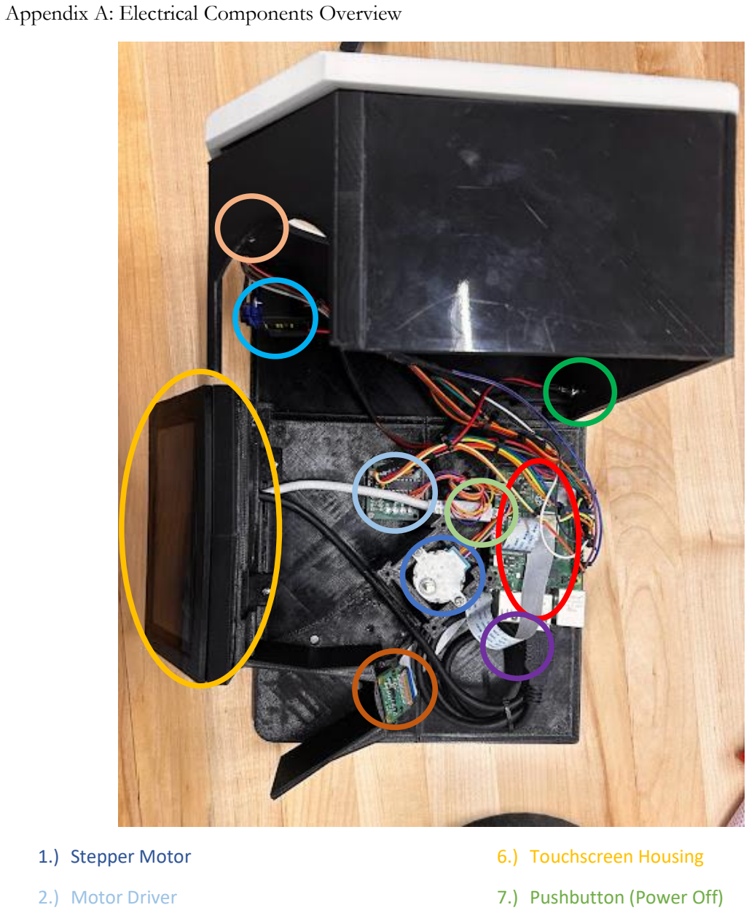
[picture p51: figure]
Appendix A: Electrical Components Overview; 1.) Stepper Motor; 2.) Motor Driver; 6.) Touchscreen Housing; 7.) Pushbutton (Power Off)

3.) Servo Motor

4.) Raspberry Pi

5.) Camera Module

8.) Pushbutton (Locking Control)

9.) Micro HDMI to HDMI

10.) USB to Micro-USB

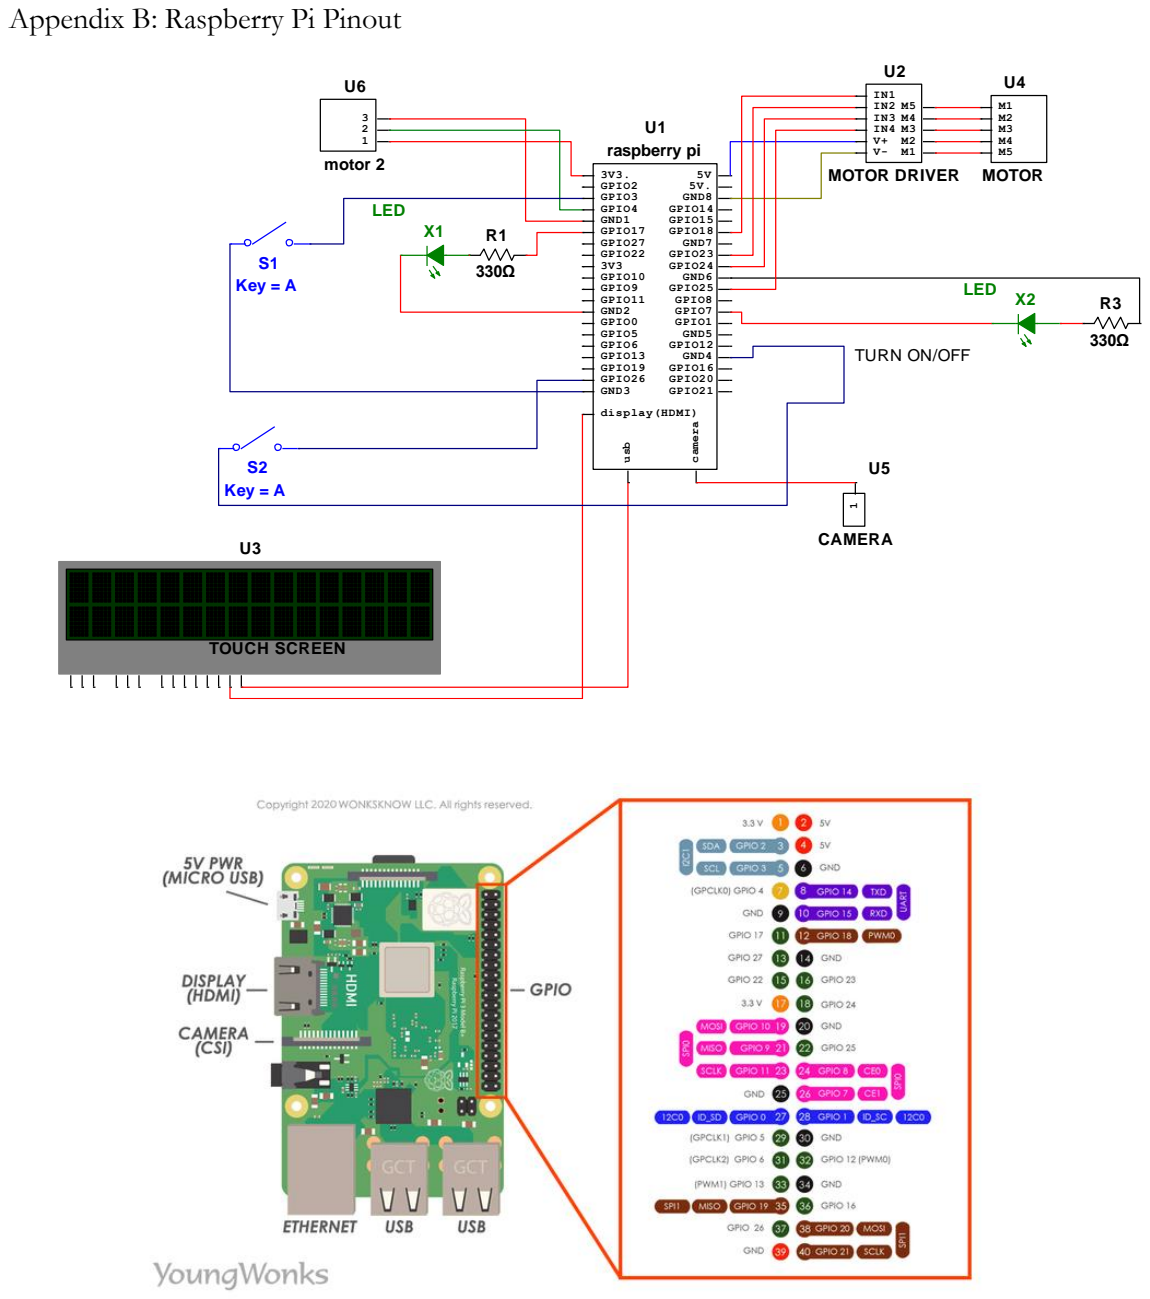
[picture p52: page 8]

Appendix B: Raspberry Pi Pinout

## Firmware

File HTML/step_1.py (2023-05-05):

#Code for the just one rotation of the stepper motor

import RPi.GPIO as GPIO
import time
 
GPIO.setmode(GPIO.BCM)
GPIO.setwarnings(False)
coil_A_1_pin = 18 # pink
coil_A_2_pin = 23 # orange
coil_B_1_pin = 24 # blue
coil_B_2_pin = 25 # yellow
 
# adjust if different
StepCount = 8
Seq = r= [[0 for x in range(4)] for y in range(StepCount)] 
Seq[0] = [1,0,0,1]
Seq[1] = [1,0,0,0]
Seq[2] = [1,1,0,0]
Seq[3] = [0,1,0,0]
Seq[4] = [0,1,1,0]
Seq[5] = [0,0,1,0]
Seq[6] = [0,0,1,1]
Seq[7] = [0,0,0,1]
 
#GPIO.setup(enable_pin, GPIO.OUT)
GPIO.setup(coil_A_1_pin, GPIO.OUT)
GPIO.setup(coil_A_2_pin, GPIO.OUT)
GPIO.setup(coil_B_1_pin, GPIO.OUT)
GPIO.setup(coil_B_2_pin, GPIO.OUT)
 
#GPIO.output(enable_pin, 1)
 
def setStep(w1, w2, w3, w4):
    GPIO.output(coil_A_1_pin, w1)
    GPIO.output(coil_A_2_pin, w2)
    GPIO.output(coil_B_1_pin, w3)
    GPIO.output(coil_B_2_pin, w4)
 
def forward(delay, steps):
    for i in range(steps):
        for j in range(StepCount):
            setStep(Seq[j][0], Seq[j][1], Seq[j][2], Seq[j][3])
            time.sleep(delay)
 
def backwards(delay, steps):
    for i in range(steps):
        for j in reversed(range(StepCount)):
            setStep(Seq[j][0], Seq[j][1], Seq[j][2], Seq[j][3])
            time.sleep(delay)
 
if __name__ == '__main__':
   
    delay = 3
    #steps = input("How many steps forward? ")
    steps = 23.2727
    forward(int(delay) / 1000.0, int(steps))
    #steps = input("How many steps backwards? ")
    #backwards(int(delay) / 1000.0, int(steps))

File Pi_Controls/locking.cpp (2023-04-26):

// g++ -std=c++11 -o ServoControl ServoControl.cpp -lwiringPi

#include <wiringPi.h>
#include <softPwm.h>
#include <stdio.h>

#define SERVO_MIN_MS 5
#define SERVO_MAX_MS 25
#define SERVO_MIN_ANGLE 0
#define SERVO_MAX_ANGLE 45

/* signal pin of the servo GPIO ReadAll*/ 
#define servoPin 7 //Physical pin 7

//Specific a certain rotation angle (0-180) for the servo
 void servoWrite(int pin, int angle){     
     long time = 0;
     time = ((angle*4/SERVO_MAX_ANGLE));  /* map the desired angle to time*/
     printf("%d\n", time);
     softPwmWrite(pin,time); 
     delay(time);  
 }

void locking(int value){
    //int d = 45;        //Common Delay Value

    if (value == 0){    //Unlock
        /*make servo rotate from minimum angle to maximum, use the function 
        servoWrite(int pin, int angle), increase 1 degree each time*/
         for(int i = SERVO_MIN_ANGLE; i <= SERVO_MAX_ANGLE; i++){
            servoWrite(servoPin, i);
        }
        // servoWrite(servoPin, 45);
        // //delay(d);
    }

    // if (value == 1){  //Lock
    //     /*make servo rotate from maximum angle to minimum, use the function 
    //     servoWrite(int pin, int angle), increase 1 degree each time*/
    //     // servoWrite(servoPin, 0);
    //     //  for(int i = SERVO_MAX_ANGLE; i >= SERVO_MIN_ANGLE; i--){
    //     //     servoWrite(servoPin, i);
    //     //     //delay(5);
    //     // }
    //     servoWrite(servoPin, 45);
    // //    // delay(d);  
    // }
}

int main(void)
{
    wiringPiSetup();    
    softPwmCreate(servoPin,  0, 200);
    locking(0);
    // delay(2000);
    // locking(1);
}

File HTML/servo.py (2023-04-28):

import RPi.GPIO as GPIO
import time

GPIO.setmode(GPIO.BCM)
GPIO.setwarnings(False)

servo_pin = 4
button_pin = 26
GPIO.setup(servo_pin, GPIO.OUT)
GPIO.setup(button_pin, GPIO.IN)

pwm = GPIO.PWM(servo_pin, 50)
# pwm.start(7.5)

# pwm.ChangeDutyCycle(1)
# time.sleep(1)

GPIO.setmode(GPIO.BCM)
GPIO.setup(button_pin, GPIO.IN, pull_up_down=GPIO.PUD_UP)

state = 0

if __name__ == '__main__':
    while True:
        GPIO.wait_for_edge(button_pin, GPIO.FALLING, bouncetime = 50)
        print("Button pressed!")
        print(state)

        if state == 0:
            # pwm.ChangeDutyCycle(10)
            pwm.start(7.5)
            time.sleep(0.1)
            pwm.ChangeDutyCycle(0)
            state = 1
            continue
        elif state == 1: 
            pwm.ChangeDutyCycle(6)
            time.sleep(0.1)
            pwm.ChangeDutyCycle(0)
            state = 0
            
            continue
